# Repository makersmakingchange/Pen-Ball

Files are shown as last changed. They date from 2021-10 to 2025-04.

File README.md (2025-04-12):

# Pen Ball
## Overview
This is a customizable (parametric) 3D printable writing aid. The pen ball makes it easier to grip a pen, pencil, or other writing utensil and may be useful for someone who has difficulty holding a pen or pencil directly. The diameter of the ball and the writing utensil diameter are available in different sizing and are able to be customized further if needed.

There are multiple sizes available for this device for both the device size and pen hole size. If you are requesting this device, please indicate which size you believe will work the best for you. There is a sizing guide seen below and available for download. **If you want to customize the sizes further download and save both the ".scad" and ".json" files in the same place and use OpenSCAD to edit using the instructions found in the documention folder above**

## Usage
A pen or pencil is inserted through the pen ball and is fixed in place by tightening a screw to allow for different pen sizes. The ball is held in the hand with the pen fixed to change the grip to be easier to write with. With different sizing available, this device works well with narrow writing utensils like paintbrushes or wider ones like sharpie markers. In addition, the device itself has alternate sizing to provide options for the user.

## Build Instructions
All documentation, design files, and photos can be found in this repository. 

## Verison History
See the folder labled "Version Archive" to access the previous versions of this device. The "Changelog" document will aid in noting key changes between the verisons

<!-- ABOUT MMC START -->
## About Makers Making Change
[Makers Making Change Logo](https://www.makersmakingchange.com/)

Makers Making Change is a program of [Neil Squire](https://www.neilsquire.ca/), a Canadian non-profit that uses technology, knowledge, and passion to empower people with disabilities.

Makers Making Change leverages the capacity of community based Makers, Disability Professionals and Volunteers to develop and deliver affordable Open Source Assistive Technologies.

 - Website: [www.MakersMakingChange.com](https://www.makersmakingchange.com/)
 - GitHub: [makersmakingchange](https://github.com/makersmakingchange)
 - Bluesky: [@makersmakingchange.bsky.social](https://bsky.app/profile/makersmakingchange.bsky.social)
 - Instagram: [@makersmakingchange](https://www.instagram.com/makersmakingchange)
 - Facebook: [makersmakechange](https://www.facebook.com/makersmakechange)
 - LinkedIn: [Neil Squire Society](https://www.linkedin.com/company/neil-squire-society/)
 - Thingiverse: [makersmakingchange](https://www.thingiverse.com/makersmakingchange/about)
 - Printables: [MakersMakingChange](https://www.printables.com/@MakersMakingChange)

### Contact Us
For technical questions, to get involved, or to share your experience we encourage you to [visit our website](https://www.makersmakingchange.com/) or [contact us](https://www.makersmakingchange.com/s/contact).
<!-- ABOUT MMC END -->

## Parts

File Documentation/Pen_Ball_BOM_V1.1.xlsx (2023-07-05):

Pen Ball |  | Total Cost | Total Print time (hr) | Total filament (g)
Version: V1.1 | Last Updated: 2023-Jun-30 | $3.07 | 8.33 | 47
Commercial Parts:
Part type (Electrical. Mechanical, Sanitization, ect) | Part Name | Quantity Needed | Pkg Quantity | Price per package | Price per Unit | Price for qty needed | Link
Hardware | M4- 0.70 Machine Screw Nut | 4 | 16 | $2.97 | $0.19 | $0.74 | https://www.homedepot.ca/product/paulin-metric-hex-nut-m4-70-16pcs/1001588036
Hardware | M4- 0.70 X 16 Machine Screw | 4 | 12 | $3.47 | $0.29 | $1.16 | https://www.homedepot.ca/product/paulin-pan-square-machine-screw-m4-70-x-16-12pcs/1001588009
3D Printed Parts ESTIMATED PRICING USING 1KG ROLL COST: | $25.00
Part | Description | Quantity Needed | TOTAL Mass (g) | Estimated Price | Print Time (Min) | Link
x_Pen_ball_y_Pen_hole.STL Where “x” is the pen ball sizing and “y” is the pen hole sizing | Pen ball STL includes both top and bottom of pen ball | 1 | 47 | $1.18 | 500
 |  |  | Total Print Cost: | $1.18
Tools for Assembly
3D Printer
Screw Driver
Alternatives (if there are other sources for some parts link them below)
Part and description | Link
Note that some printers are less accurate and M4 size hardware may not fit. It is recommended that you go to a hardware store and test different bolt sizes for the palm pen that is created

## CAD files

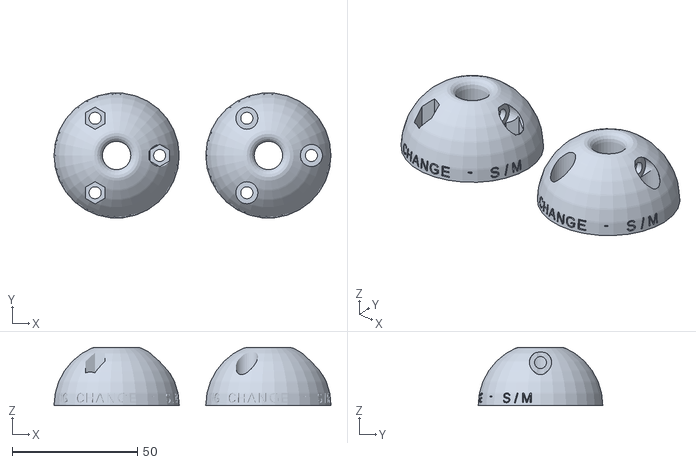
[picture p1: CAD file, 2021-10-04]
3D print files/Small_Pen_ball_Medium_Pen_hole.stl
110.4 x 49.7 x 23.2

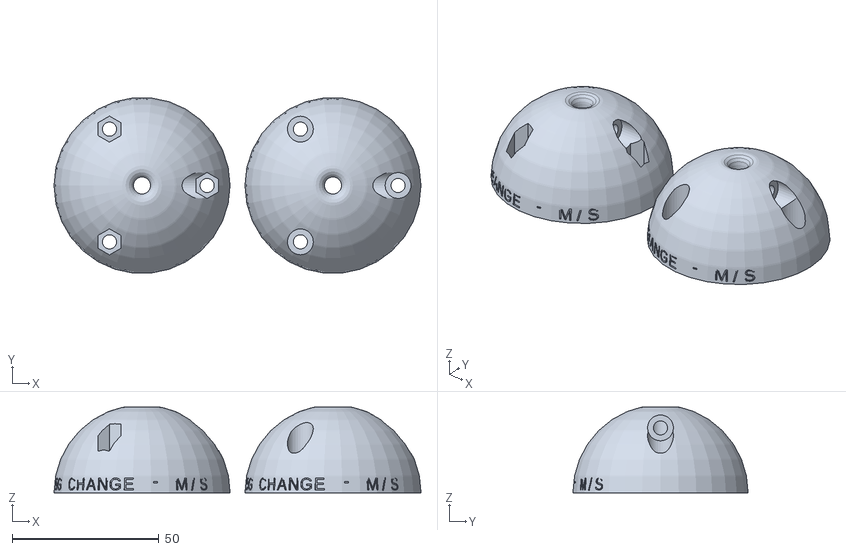
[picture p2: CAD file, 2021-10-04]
3D print files/Medium_Pen_ball_Small_Pen_hole.stl
124.9 x 59.6 x 29.3

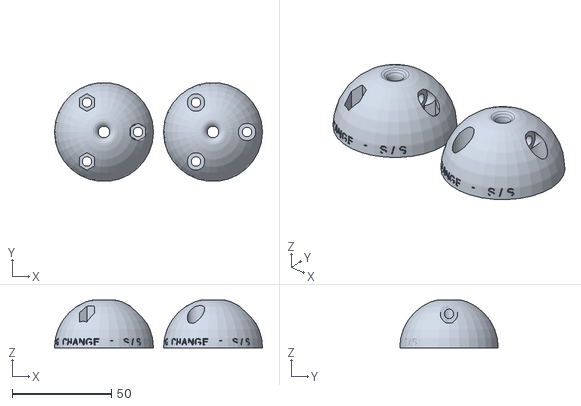
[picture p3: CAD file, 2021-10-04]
3D print files/Small_Pen_ball_Small_Pen_hole.stl
104.9 x 49.7 x 24.1

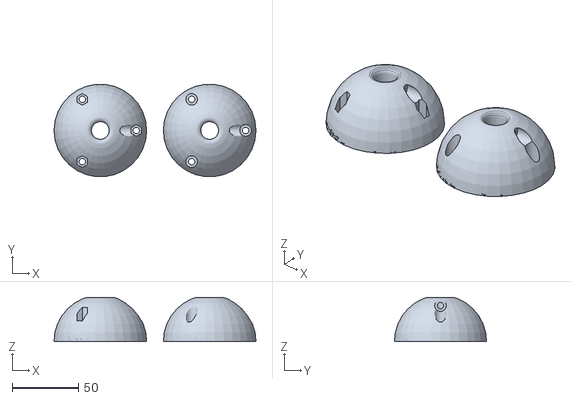
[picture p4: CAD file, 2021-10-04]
3D print files/Large_Pen_ball_Large_Pen_hole.stl
152.4 x 69.6 x 33.3

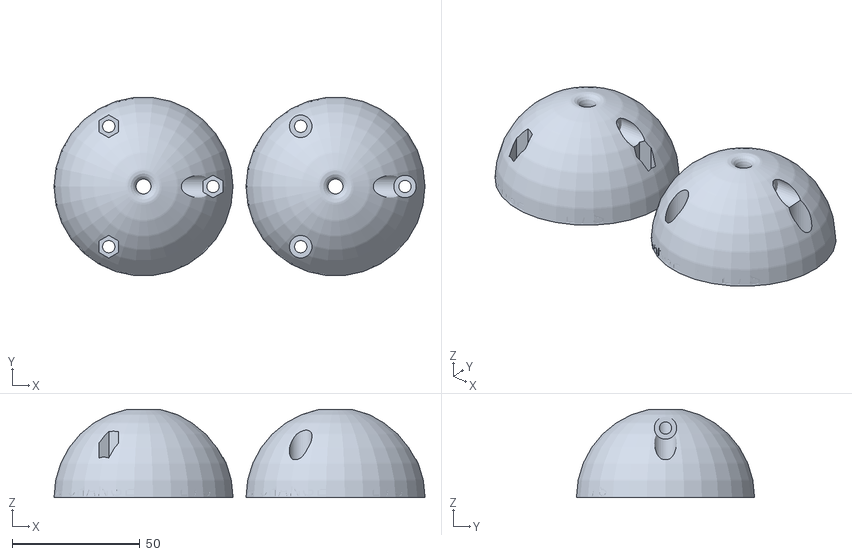
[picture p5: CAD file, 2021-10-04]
3D print files/Large_Pen_ball_Small_Pen_hole.stl
144.9 x 69.6 x 34.4

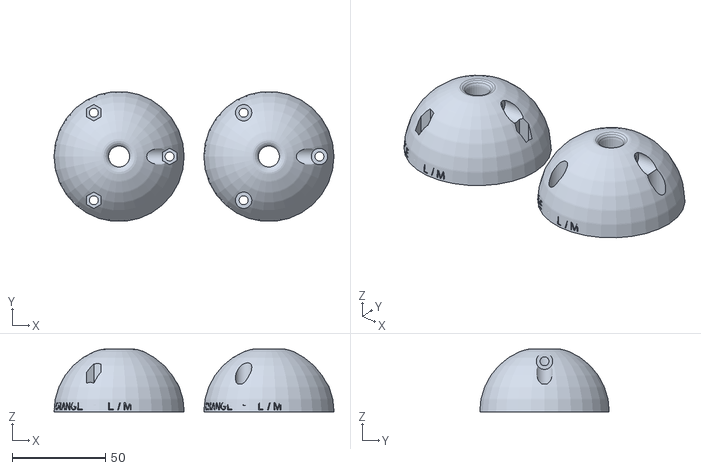
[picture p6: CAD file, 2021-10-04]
3D print files/Large_Pen_ball_Medium_Pen_hole.stl
150.4 x 69.6 x 33.6

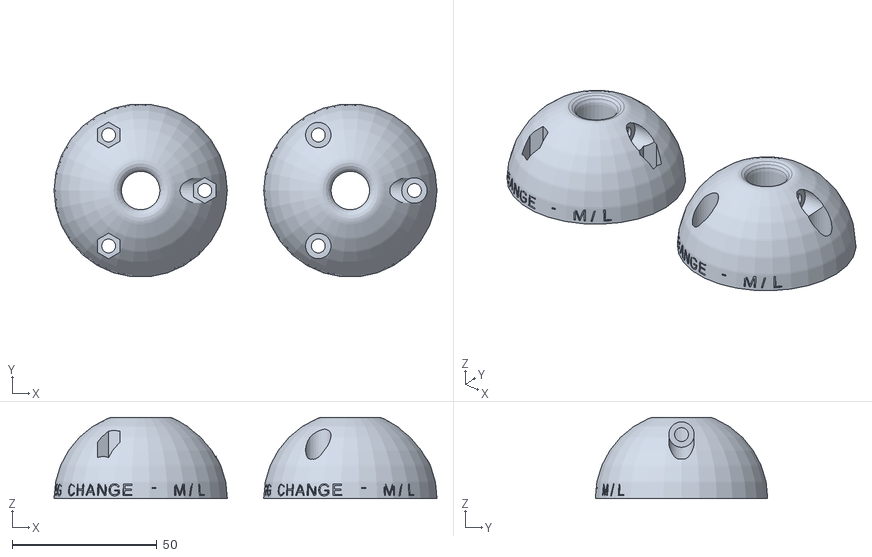
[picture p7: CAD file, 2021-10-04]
3D print files/Medium_Pen_ball_Large_Pen_hole.stl
132.4 x 59.6 x 28.1

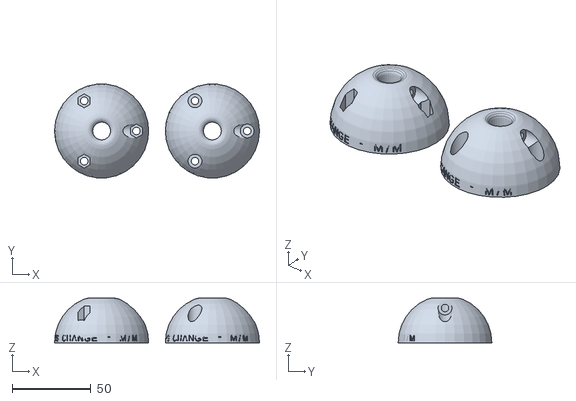
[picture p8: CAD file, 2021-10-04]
3D print files/Medium_Pen_ball_Medium_Pen_hole.stl
130.4 x 59.6 x 28.4

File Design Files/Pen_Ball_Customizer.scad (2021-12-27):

// parametric pen ball - scruss 2018-03
// CC BY-SA - Stewart Russell - scruss.com
// for Makers Making Change - http://makersmakingchange.com/

// you will need:
// * 5 off M4 x 12 stainless pan head machine screws
// * 5 off M4 stainless nuts

// ** the two main parameters **
// may produce a useless design, so change at your own risk
ball_diam = 60.0;   // 60 mm is default; can go to 45 if wall_thick reduced
pen_diam = 10.5;    // should fit most pens; 10.5 mm is default

// ** lesser parameters
wall_thick = 2.0;   // shell thickness; default 2, reduce to 1 for 45 mm diameter
tol=0.8;            // tolerance for loose fit
// *** NB: please do not explicitly set $fn ***
// and everything below here: HERE BE (smallish) DRAGONS

/* M4 nut and screw dimensions - sized for M4 x 12

Nut: 7 mm across flats, 3.2 mm thick
so across points = 7 / ((√3) / 2) ~= 8.1 mm
source: http://www.fairburyfastener.com/xdims_metric_nuts.htm

Screw:          4.0 mm, 4.7 to outside of thread
Length:        12 or 20 mm
Head height:    3.1 mm
Head diameter:  8.0 mm
source: https://spaenaur.com/pdf/sectionR/R11.pdf
*/
nut_thick =          3.2;
nut_flats =          7.0;
nut_diam =          nut_flats / (sqrt(3)/2);
screw_length =      12.0;            // M4 x 12
screw_nom_diam =     4.0;
screw_head_diam =    8.0;
screw_head_thick =  nut_thick;   // for simplicity
pillar_height =     screw_length - (1.25 * nut_thick);

/* bolt passages:
   since we're on a sphere, the height at
   radius x is given by
   
   y = 2 × √(r² - x²)
   
   this drops off very quickly as x → r
   so we probably won't need this
*/
function height_at_radius(d, r) = 2 * sqrt(pow(d / 2, 2) - pow(r, 2));
pillar_diam = nut_diam + 2 * tol + wall_thick;
pillar_at_radius = (ball_diam - 2 * wall_thick - pillar_diam) / 2;
height_at_pillar = height_at_radius(ball_diam, pillar_at_radius);
catch_offset = pillar_at_radius;
echo(pillar_diam=pillar_diam, pillar_at_radius=pillar_at_radius, height_at_pillar=height_at_pillar, catch_offset=catch_offset);

//engraving variables
chars = "MAKERS MAKING CHANGE";
chars2 = "MAKERSMAKINGCHANGE.COM";
radius = (ball_diam/2)-3;
myPi = 3.14159;
chars_per_circle = 40;
step_angle = 360 / chars_per_circle;
circumference = 2 * PI * radius;
char_size = circumference / chars_per_circle;
char_thickness = 1;

module inprofile() {
    // rather than using a sphere, rotate_extrude a 2D path
    offset(r=-3 * wall_thick/2, $fn=16)difference() {
        circle(d=ball_diam, center=true, $fn=32);
        translate([-(ball_diam-(pen_diam + tol))/2, 0])square(ball_diam, center=true);
    }
}

module profile() {
    // 2D path for profile; looks like a letter D, kinda
    union() {
        difference() {
            offset(r=3 * wall_thick / 2, $fn=16)inprofile();
            offset(r=wall_thick / 2, $fn=16)inprofile();
        }
        translate([ball_diam / 2 - wall_thick, 0])square(wall_thick, center=true);
    }
}

module pillars() {
    // solid pillars we shoot the screw/nut holes through
    for(i=[0:2]) {
        rotate([0, 0, i * 120])translate([pillar_at_radius, 0, 0])cylinder(d=pillar_diam, h=2*height_at_pillar, center=true);
    }
}
            
module stiffeners() {
    // pen pipe stiffeners: two, 120 deg apart
    for(i=[0:1]) {
        rotate([0,0,30 + i * 120])rotate([-90, 0, 0])translate([0, 0, (pen_diam + wall_thick)/2])cylinder(d=screw_nom_diam, h=pillar_at_radius);
    }
}

module catch_reinforce() {
    // this is ugly: make a block to take pen-holding screw/nut
    //  but angled so you can print without support
    rotate([90, 0, 0])linear_extrude(height=pillar_diam, center=true)polygon([
    [ pen_diam / 2, catch_offset ],
    [ pen_diam / 2, catch_offset - pillar_diam / 2],
    [ pillar_at_radius, 0 ],
    [ pen_diam / 2, -(catch_offset - pillar_diam / 2)],
    [ pen_diam / 2, -catch_offset ],
    [ pen_diam / 2, -ball_diam/2 ],
    [ ball_diam/2, -ball_diam/2 ],
    [ ball_diam/2, ball_diam/2 ],
    [ pen_diam / 2, ball_diam/2 ],
    ]);
}

module inside_bits() {
    // all of the interior detail, clipped to the outer shell size
    intersection() {
        union() {
            stiffeners();
            pillars();
            catch_reinforce();
        }
        rotate_extrude()offset(r=wall_thick, $fn=16)inprofile();
    }
}

module screw_holes() {
    // three holes around edge: these are negative spaces
    // nut holes have six sides ('cylinder ... $fn=6') as
    // we emulate hex nuts that way: low-poly cylinders!
    for(i=[0:2]) {
        translate([pillar_at_radius * cos(i * 120), pillar_at_radius * sin(i * 120), 0]) {
            cylinder(d=screw_nom_diam + tol, h=ball_diam, center=true, $fn=32);
            translate([0, 0, pillar_height/2])rotate([0, 0, 30])cylinder(d=nut_diam + tol, h=ball_diam, $fn=6);
            translate([0, 0, -1*(ball_diam + pillar_height/2)])cylinder(d=screw_head_diam + tol, h=ball_diam, $fn=32);
        }
    }
}

module nut_catches() {
    // negative space for pen grip screw holes and nut catches
    // top screw hole
    translate([0, 0, catch_offset])rotate([90, 0, 90])union() {
        cylinder(d=screw_nom_diam + tol, h=ball_diam, $fn=32);
        translate([0,0,screw_length+1])cylinder(d=screw_head_diam + tol, h=ball_diam, $fn=32);
        // top nut catch
        translate([0,0,(pen_diam + tol + wall_thick) / 2])hull() {
            rotate([0, 0, 30])cylinder(d=nut_diam + tol, h=nut_thick + tol, $fn=6);
            translate([0, -ball_diam / 2, 0])rotate([0, 0, 30])cylinder(d=nut_diam + tol, h=nut_thick + tol, $fn=6);
        }
    }
    // bottom screw hole
    translate([0, 0, -catch_offset])rotate([90, 0, 90])union() {
        cylinder(d=screw_nom_diam + tol, h=ball_diam, $fn=32);
        translate([0,0,screw_length+1])cylinder(d=screw_head_diam + tol, h=ball_diam, $fn=32);
        // bottom nut catch
        translate([0,0,(pen_diam + tol + wall_thick) / 2])hull() {
            rotate([0, 0, 30])cylinder(d=nut_diam + tol, h=nut_thick + tol, $fn=6);
            translate([0, ball_diam / 2, 0])rotate([0, 0, 30])cylinder(d=nut_diam + tol, h=nut_thick + tol, $fn=6);
        }
    }
}

module shell() {
    // assemble all the things!
    difference() {
        union() {
            // the positive bits
            rotate_extrude()profile();  // outer shell
            inside_bits();              // interior detail
			}
			//engraving text
			for(i = [0 : chars_per_circle - 1]) {
    rotate(i * step_angle) 
        translate([0, radius + char_size / 2, 3]) 
            rotate([90, 0, 180]) linear_extrude(char_thickness) text(
                chars[i], 
                font = "Courier New; Style = Bold", 
                size = char_size, 
                valign = "center", halign = "center"
            );
        }//for (end engraving)
        union() {
            // the negative bits
            screw_holes();              // edge holes
            nut_catches();
        }
    }
}

module slice() {
    // split ball across middle and place halves side by side
    // (lower half flipped) for easy printing
    union() {
        translate([-(ball_diam + pen_diam) / 2, 0, 0]) {
            difference() {
                shell();
                translate([0, 0, -0.6 * ball_diam])cube(1.2 * ball_diam, center=true);
                			//engraving text
			for(i = [0 : chars_per_circle - 1]) {
    rotate(i * step_angle) 
        translate([0, radius + char_size / 2, 3]) 
            rotate([90, 0, 180]) linear_extrude(char_thickness) text(
                chars[i], 
                font = "Courier New; Style = Regular", 
                size = char_size, 
                valign = "center", halign = "center"
            );
        }//for (end engraving)
				}
        }
        translate([(ball_diam + pen_diam) / 2, 0, 0]) {
            difference() {
                rotate([180, 0, 0])shell();
                translate([0, 0, -0.6 * ball_diam])cube(1.2 * ball_diam, center=true);
							//engraving text
			for(i = [0 : chars_per_circle - 1]) {
    rotate(i * step_angle) 
        translate([0, radius + char_size / 2, 3]) 
            rotate([90, 0, 180]) linear_extrude(char_thickness) text(
                chars2[i], 
                font = "Courier New; Style = Bold", 
                size = char_size, 
                valign = "center", halign = "center"
            );
        }//for (end engraving)
            }
        }
    }
}

slice(); // generate the sliced module

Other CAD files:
3D print files/Small_Pen_ball_Large_Pen_hole.stl
Version Archive/Version 1/Pen_Grip_Ball.stl
Version Archive/Version 1/Pen_Grip_Ball.scad

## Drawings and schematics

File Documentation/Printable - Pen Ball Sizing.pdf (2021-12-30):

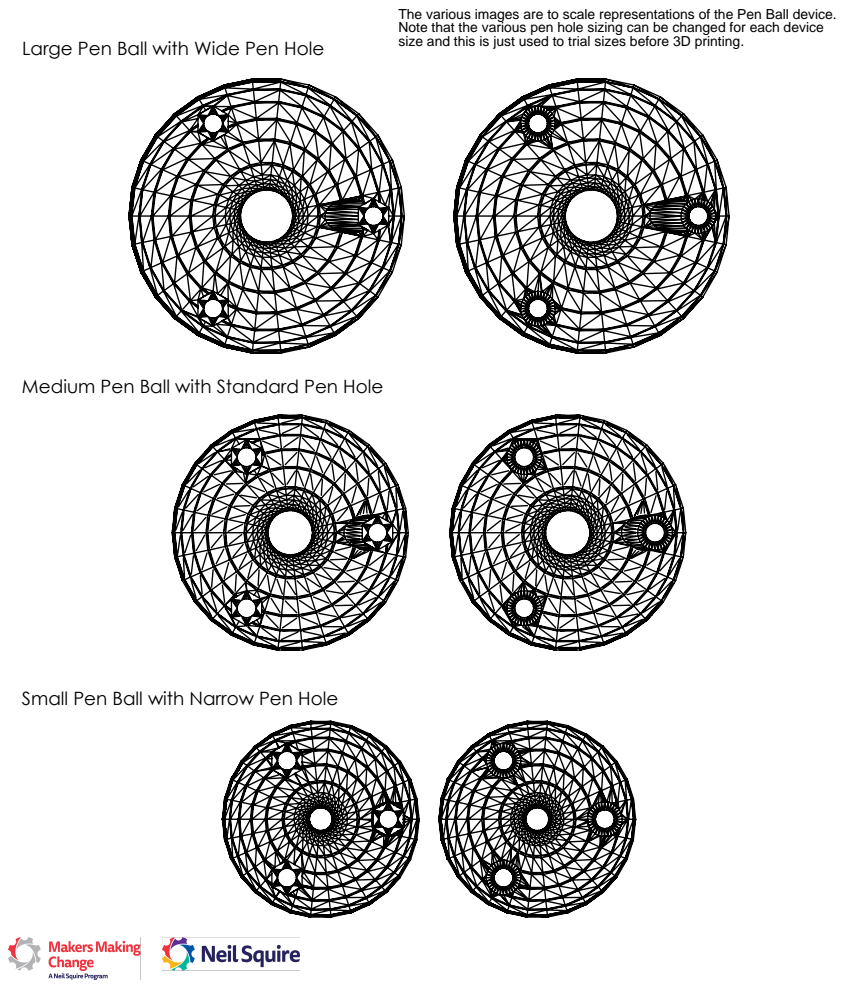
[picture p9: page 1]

The various images are to scale representations of the Pen Ball device.
Note that the various pen hole sizing can be changed for each device
size and this is just used to trial sizes before 3D printing.

Large Pen Ball with Wide Pen Hole

Medium Pen Ball with Standard Pen Hole

Small Pen Ball with Narrow Pen Hole

SOLIDWORKS Educational Product. For Instructional Use Only.

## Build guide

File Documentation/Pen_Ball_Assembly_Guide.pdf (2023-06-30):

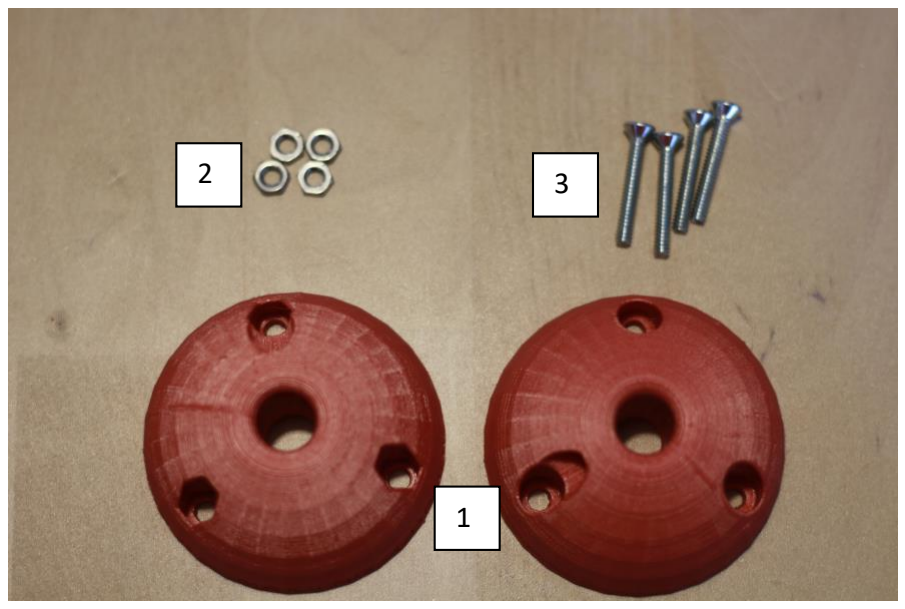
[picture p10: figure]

© 2023 by <Author>. This work is licensed under the CC BY SA 4.0 License: http://creativecommons.org/licenses/by-sa/4.0
Files available at <Replace with MMC Library Link> | Page 1 of 4
V1.1 | June 2023

# Pen Ball

# ASSEMBLY GUIDE

### Video for assembly can be found here: https://www.youtube.com/watch?v=FC61UELQ8Oo&list=PLhoPg9bDvBR61-

Vq6Jozt5OBoi0aSeOWO&index=16 (https://www.youtube.com/watch?v=FC61UELQ8Oo&list=PLhoPg9bDvBR61-Vq6Jozt5OBoi0aSeOWO&index=16)

## Required Components

### Required Materials:

### 1. 1x 3D Printed Top and Bottom of Pen Ball

2. 5x M4- 0.70

### Machine Screw Nut 3. 5x M4- 0.70 X 16 Machine Screw

### Note: only 4 machine screw nuts and screws are shown here but 5 is the desired quantity

## Required Tools

### - 3D printer - Screwdriver

## Required Personal Protective Equipment (PPE)

### - Safety Glasses

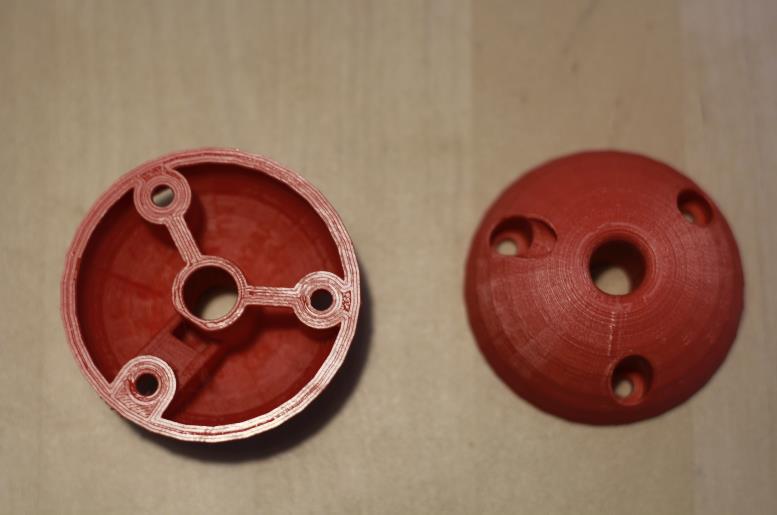
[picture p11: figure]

Files available at <Replace with MMC Library Link> | Page 2 of 4
V1.1 | June 2023

# Pen Ball

# ASSEMBLY GUIDE

Assembly Instructions

Step 1
Gather materials needed and ensure that all of the holes in the Pen Ball halves are not obstructed by extra filament. If they are attempt to remove extra filament.

V1.1 | June 2023

# Pen Ball

# ASSEMBLY GUIDE

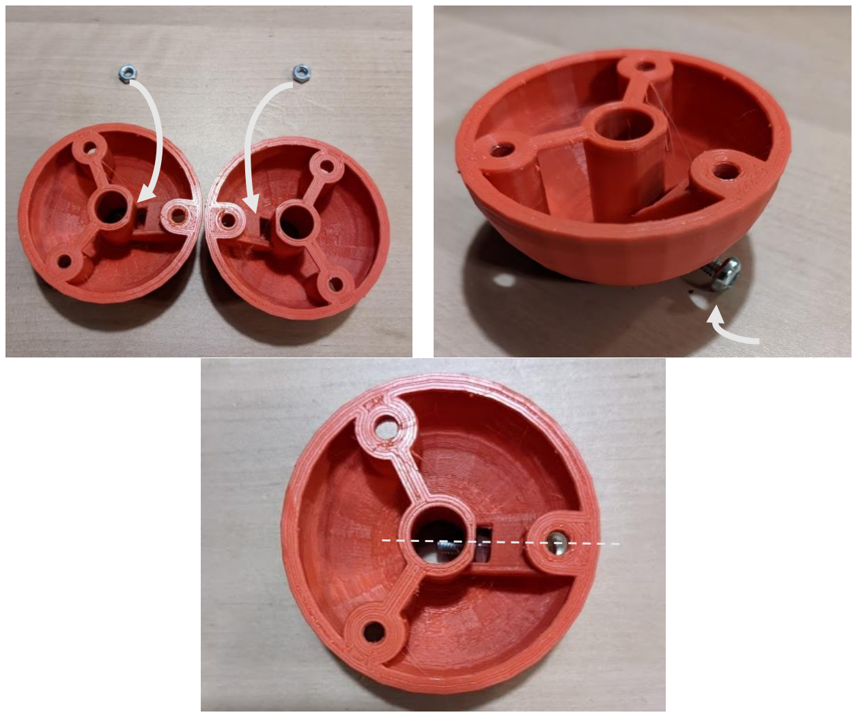
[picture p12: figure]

Files available at <Replace with MMC Library Link> | Page 3 of 4
Step 2
Insert the set screw nut into the rectangular slot on the inside of the pen ball halves. Now gently thread on the set screw so the nut is held in place. Do this for both halves of the Pen Ball.
Step 3
Put the two halves of the pen ball together lining up the bolt holes. One-half of the pen ball has hexagon shaped hole and the other has a smooth circle hole. Push the threads of the M4 screws into the rounded hole and out through the hexagon shaped hole. Then place a nut on the end of that machine screw on the hexagon side and tighten until snug. Repeat for other three holes.

# Pen Ball

# ASSEMBLY GUIDE

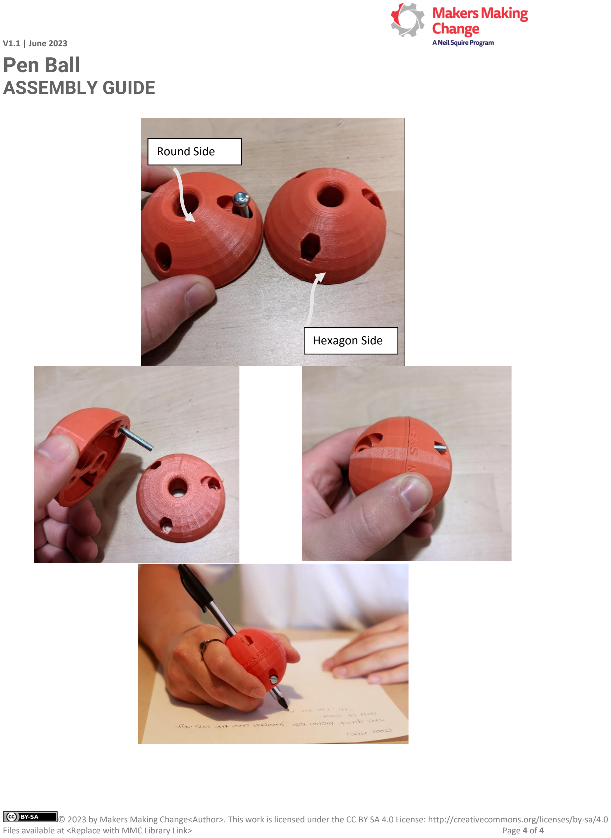
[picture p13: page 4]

V1.1 | June 2023

© 2023 by Makers Making Change<Author>. This work is licensed under the CC BY SA 4.0 License: http://creativecommons.org/licenses/by-sa/4.0
Files available at <Replace with MMC Library Link> | Page 4 of 4

### Hexagon Side

### Round Side

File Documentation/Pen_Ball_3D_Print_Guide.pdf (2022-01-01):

V1.0 | Sept 2021

## Pen Ball

## 3D PRINTING GUIDE

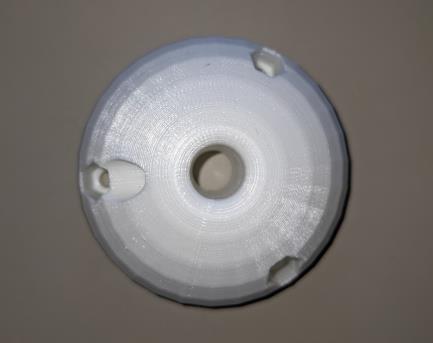
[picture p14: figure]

© 2021 by <Author>.

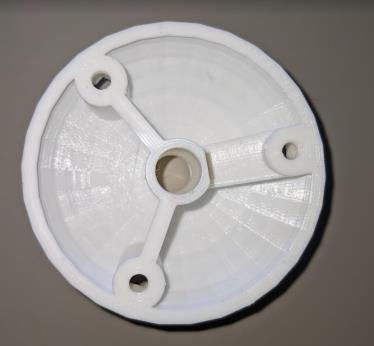
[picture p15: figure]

This work is licensed under the CC BY SA 4.0 License: http://creativecommons.org/licenses/by-sa/4.0
Files available at <Replace with MMC Library Link> | Page 1 of 1

### 3D Printing Summary

Pen Ball Size
Metrics | Small | Medium | Large
Total Print Time (min) | 240 | 360 | 500
Total Number of Components | 2 | 2 | 2
Typical Total Mass (g) | 25 | 35 | 47
Typical Number of Print Setups | 1 | 1 | 1

### 3D Printing Settings

Print File Name | Qty | Total Print Time (hr:min) | Mass (g) | Infill (%) | Support (Y/N) | Layer Height/ Nozzle Diameter (mm) | Notes (orientation, special settings, etc)
x_Pen_ball_y_Pen_hole.STL where “x” is the pen ball sizing and “y” is the pen hole sizing | 1 | 240-500 | 25-48 | 20 | N | 0.2/0.4 | - Print in orientation given when brought onto slicer bed

### Post-Processing

- If you notice any blobs on the side of the device try using a blade to clean up the prints.

### Customization Options

- If different sizing is required for the pen hole or palm pen diameter the sizes can be altered using the OpenSCAD file found on the GitHub “design files” folder. Access to the GitHub can be found on the project page of this device.

### Examples of Quality Prints:

- Below are photos of what print quality is expected from printing this device.

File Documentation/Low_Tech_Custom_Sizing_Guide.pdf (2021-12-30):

V1.0 | <Sept> <2021>

## Pen Ball/Palm Pen Holder

## OPENSCAD CUSTOM SIZING GUIDE

© 2021 by <Author>. This work is licensed under the CC BY SA 4.0 License: http://creativecommons.org/licenses/by-sa/4.0
Files available at <Replace with MMC Library Link> | Page 1 of 2

### Overview

To create custom Pen Ball or Palm Pen Holder sizing OpenSCAD is an excellent and easy to use tool to create STLS within minutes. If a user requires a alternate size of device to fit a specific need this tool can be used to adapt the current small, medium, and large sizes,

### Creating Custom Sized Assistive Tech:

### Step 1: Downloading OpenSCAD

- The download link for OpenSCAD can be found here: https://openscad.org/downloads.html
- The software is free and available on Windows, MacOS, and Linux

### Step 2: Open the OpenSCAD File

- Once OpenSCAD is downloaded, locate the “Palm_Pen_Custom_Sizing.scad” or the “Pen_Ball_ Custom_Sizing.scad” file (depending on the device you are trying to edit) on the GitHub page and double click it to open the file in OpenSCAD.
- Ensure to download the second file that will be in the same folder with the “.json” file type. This must be downloaded in the same place as the “.scad” file. This will never need to be opened but contains all the preset custom sizings.

### Step 3: Finding Current Standard Sizing

- Each device size (small, medium, or large) has a option of also having a small, medium, or large pen hole size. This creates 9 different options for the device sizing.
- The STL’s for these sizes have already been made and can be found on the project pages GitHub
- If you want to view the sizing in more detail on OpenSCAD you can look to the top right of the screen to see the customizer “presets” seen below.
- The naming convention of the presets are “x w y Device Name” where x and y are the device size and the pen hole size respectively and w stands for “with”. So for example one preset could be “medium w large pen hole”
- After selecting one of the presets give the software a moment to reload the new dimensions, to see the dimensions click the “parameter” button below

V1.0 | <Sept> <2021>

## Pen Ball/Palm Pen Holder

## OPENSCAD CUSTOM SIZING GUIDE

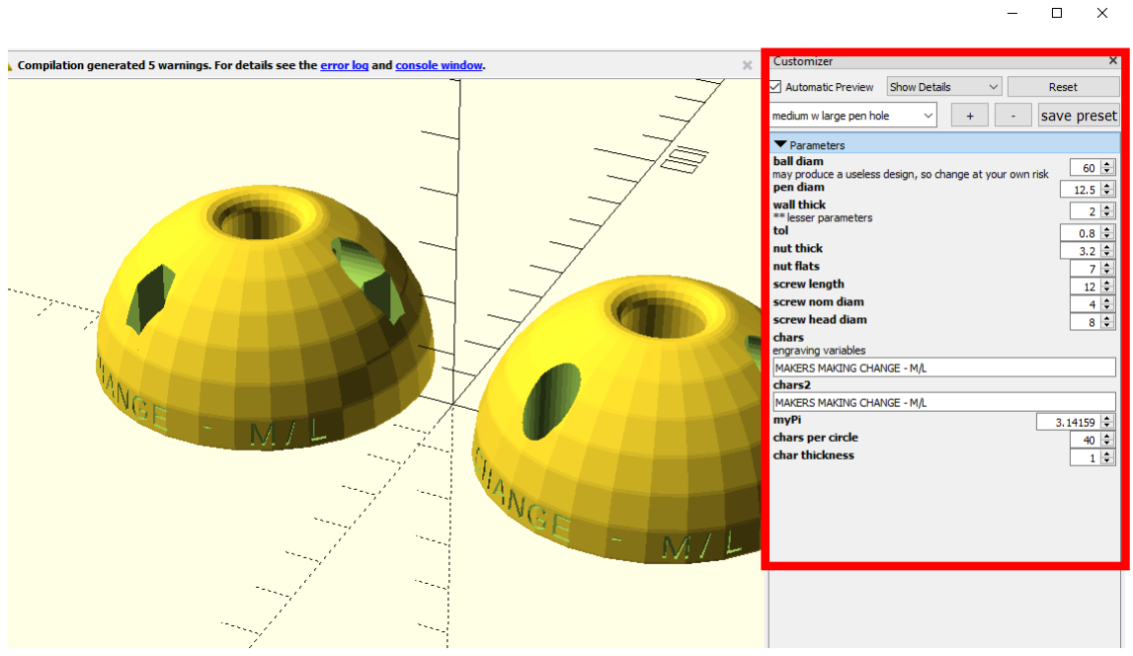
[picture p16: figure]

© 2021 by <Author>. This work is licensed under the CC BY SA 4.0 License: http://creativecommons.org/licenses/by-sa/4.0
Files available at <Replace with MMC Library Link> | Page 2 of 2

### Step 4: Customizing Standard Sizing

- Pick the preset you want to change the dimensions of
- Open the parameters tab and edit the dimensions to suit the needs of the user of the device
- Be careful that changing the dimensions outside the ranges of small, medium, and large may result in a part that does not print well so make sure that when the parts are changed the device will still work as intended when it is printed

### Step 5: Creating the 3D Printable Braille Model

- Once step 4 is complete and you are happy with the model you have created, click on the “Preview” button at the top of the text pane to view your model. This looks like a cube with two arrows going to the right.
- If everything looks correct and the model loads without error, click the “Render” button to prepare your model. If you’re not ready, make the necessary edits and then hit “Preview” again.
- After rendering the model, you’re ready to export the file. Click on the “Export as STL” button and save the file. This file can now be used to 3D print. Please see 3D Printing Guide document for tips on printing Braille.

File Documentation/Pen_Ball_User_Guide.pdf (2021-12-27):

V1.0 | September 2021

## Pen Ball

## USER QUICK GUIDE

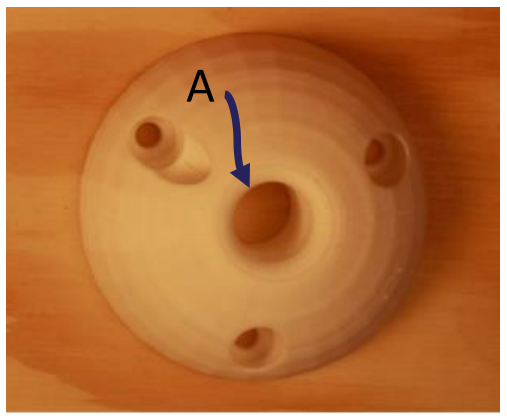
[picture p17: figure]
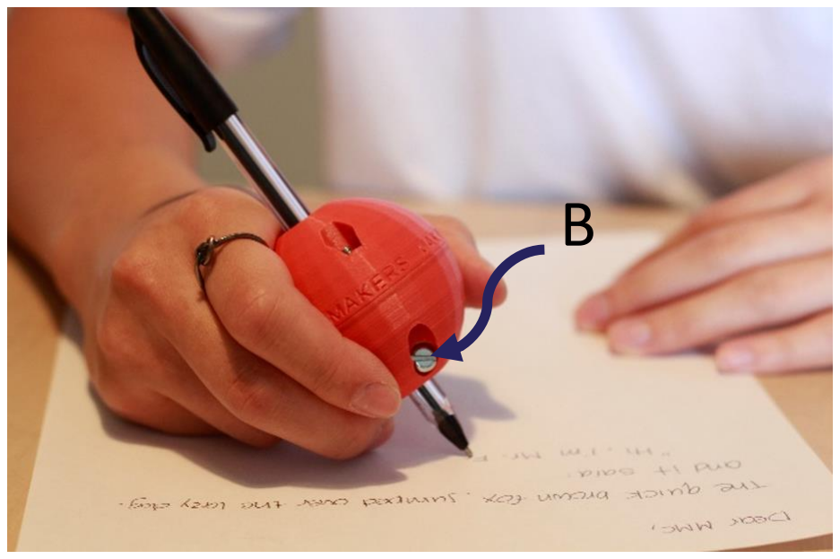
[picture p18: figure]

© 2021 by <Author>. This work is licensed under the CC BY SA 4.0 License: http://creativecommons.org/licenses/by-sa/4.0
Files available at <Replace with MMC Library Link> | Page 1 of 4

### Introduction

The Pen Ball device creates a wider grip for users who struggle to use writing utensils that require a tight pinch grip. The Pen Ball comes in a few predetermined sizes large, medium, and small with each size also having a pen hole size of small, medium, and large. This allows users with different hand sizes/shapes as well as including different pen sizes allows for a variety of use cases. Custom sizing can also be done by requesting the maker to use the OpenSCAD file on the project page to adjust the dimensions. If you want specific sizing information of the pen ball, a sizing guide can be found at the bottom of this document.

### Features

The pen ball is made up of two halves that are attached together to form a sphere. This sphere has a hole through the middle of it called a “pen hole” [A]. A writing utensil, paintbrush, or any cylindrical device can be put through the pen hole and fixed using the two set screws [B] found on the side of the device.

### Usage

The Pen Ball requires a writing utensil to be inserted into the pen hole. The writing utensil can then be fixed in the desired positon by tightening the set screws. The Pen Ball is then ready to use and can be held in any orientation the user desires for their ideal grip.

### Compatibility

Set screws allow many sizes of writing utensils to be placed into the pen hole. In addition, if you find that the set screws are not able to secure the writing utensil or it is not able to fit inside the pen hole the varying sizes of pen hole (small, medium, or large) can be 3D printed/requested to allow for these cases.

## USER QUICK GUIDE

Files available at <Replace with MMC Library Link> | Page 2 of 4

### Cleaning

The pen ball can be sprayed or wiped down with sanitizing cleaners. Do not wash the Pen Ball in high heat as it can cause it to melt or break. (i.e. do not use Dishwashers, soaking in hot water, washing machines)

### Specifications

The sizing guide for the Pen Ball can be seen on the next page:

## USER QUICK GUIDE

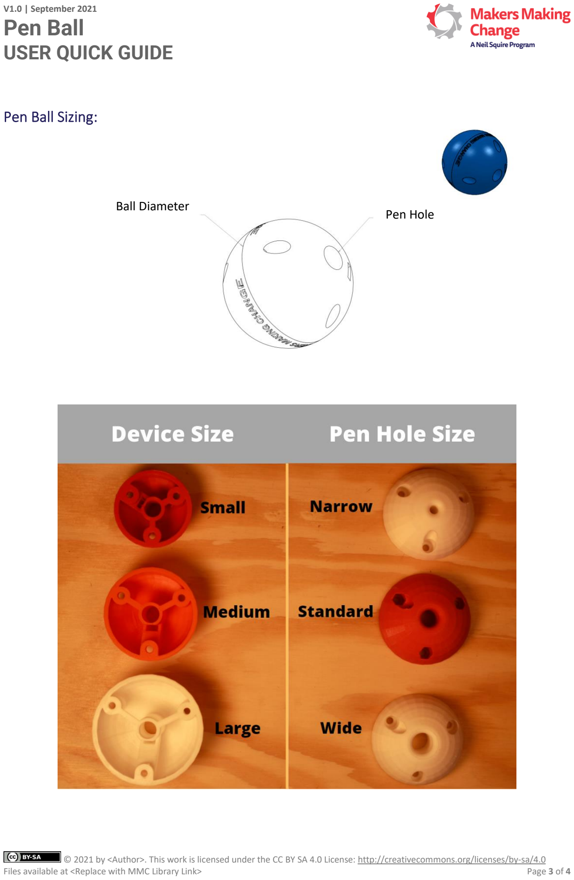
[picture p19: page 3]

Files available at <Replace with MMC Library Link> | Page 3 of 4

### Pen Ball Sizing:

Ball Diameter | Pen Hole

## USER QUICK GUIDE

Files available at <Replace with MMC Library Link> | Page 4 of 4
Palm pen version | Pen hole size | Ball Diameter (mm) | Pen Hole (mm)
Small Pen Ball | Narrow | 50 | 5
| Standard | 50 | 10.5
| Wide | 50 | 12.5
Medium Pen Ball | Narrow | 60 | 5
| Standard | 60 | 10.5
| Wide | 60 | 12.5
Large Pen Ball | Narrow | 70 | 5
| Standard | 70 | 10.5
| Wide | 70 | 12.5

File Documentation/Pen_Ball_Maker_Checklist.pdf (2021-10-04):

V1.0 | September 2021

## Pen Ball

## MAKER CHECKLIST

© 2021 by <Author>.
This work is licensed under the CC BY SA 4.0 License: http://creativecommons.org/licenses/by-sa/4.0
Files available at <Replace with MMC Library Link> | Page 1 of 1

## Maker To Do List

Determine the size of pen ball the requester wants based off of sizing chart
Determine the cost of materials and relay this cost to the user before purchasing to ensure the requester is comfortable with the price
Ask requester if they want any customizations to the device (color, size, specific writing utensil) Print and purchase the required materials
Assemble the device
Deliver the device and User Guide to the requester

## Items to Give to User

User Guide
Pen Ball

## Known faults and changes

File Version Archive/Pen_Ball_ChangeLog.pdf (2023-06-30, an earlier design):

© 2021 by <Author>. This work is licensed under the CC BY SA 4.0 License: http://creativecommons.org/licenses/by-sa/4.0
Files available at <Replace with MMC Library Link> | Page 1 of 1

V1.1| June 2023

## Pen Ball

## CHANGELOG

## Version 1 | Date unknown

- Pen ball with thinner walls and lesser print times
- OpenSCAD file for customization
- Created by Stewart Russel

## Version 2 | Date 09/15/2021

- Updated documentation
- Small, medium, large sizes for device and narrow, standard, and wide pen holes created with extra documentation around using the OpenSCAD file for customization

## Version 3 (Current Version) | Date 06/30/2023

## - Updated documentation
